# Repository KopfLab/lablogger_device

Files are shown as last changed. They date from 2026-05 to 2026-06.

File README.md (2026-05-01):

# *labLogger*

This repository holds the code, schematics, and documentation to build lab loggers. All content of this repository is free to use for noncommercial research and development efforts as outlined in the terms of the included [LICENSE file](LICENSE.md).

To cite ***labLogger*** in publications use:

> Kopf S, 2026. _labLogger: a Modular Internet Controllable LAB Equipment Logger_. <https://github.com/KopfLab/lablogger_device>

A BibTeX entry for LaTeX users is

```
@Manual{
  microLogger,
  title = {labLogger: a Modular Internet Controllable LAB Equipment Logger},
  author = {Sebastian Kopf},
  year = {2026},
  url = {https://github.com/KopfLab/lablogger_device}
}
```

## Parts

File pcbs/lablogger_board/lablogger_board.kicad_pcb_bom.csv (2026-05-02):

Designator | Quantity | Value | Footprint | Package | MPN | DNP | Mount_Type | Description | JLCPCB | JLCPCBURL | DigiKey | DigiKeyURL | STANDARD | MAXIMUM_PACKAGE_HEIGHT | MANUFACTURER | ParticleURL
C1, C2, C3, C4, C5, C6 | 6 | 100nF | C_0603 |  |  |  | smt | Unpolarized capacitor | C1591 | https://jlcpcb.com/partdetail/1943-CL10B104KB8NNNC/C1591
D1 | 1 | 1A/40V/500mV | D_DO-214AC_SMA |  | SS14 |  | smt | Diode 40 V 1A Surface Mount DO-214AC (SMA) | C83852 | https://jlcpcb.com/partdetail/onsemi-SS14/C83852 | SS14CT-ND | https://www.digikey.com/en/products/detail/onsemi/SS14/965474
D2, D3 | 2 | 3A/60V/750mV | D_DO-214AB_SMC |  | SS36 |  | tht | Diode 60 V 3A Surface Mount DO-214AB (SMC) | C391251 | https://jlcpcb.com/partdetail/onsemi-SS36/C391251 | SS36FSCT-ND | https://www.digikey.com/en/products/detail/onsemi/SS36/1053019
F1 | 1 | 24V/2.6A | Fuse_1812 |  | 2920L260/24DR |  | smt | Polymeric PTC Resettable Fuse 24V 2.6 A Ih Surface Mount 2920 (7351 Metric), Concave | C315904 | https://jlcpcb.com/partdetail/Littelfuse-2920L26024DR/C315904 | F6728CT-ND | https://www.digikey.com/en/products/detail/littelfuse-inc/2920L260-24DR/5427247
J10, J9 | 2 | 5mm | TERMINAL_BLOCK_1x03_5mm_vertical |  | TBP04R2-500-03BE |  | tht | 3 Position Terminal Block Header, Male Pins, Shrouded (4 Side) 0.197" (5.00mm) Vertical Through Hole |  |  | 2223-TBP04R2-500-03BE-ND | https://www.digikey.com/en/products/detail/same-sky-formerly-cui-devices/tbp04r2-500-03be/15775507 | Manufacturer Recommendations | 12.00mm
J11, J12 | 2 | DB9 | DB9_male |  | DE09P064TXLF |  | tht | 9 Position D-Sub Plug, Male Pins Connector |  |  | 609-1524-ND | https://www.digikey.com/en/products/detail/amphenol-cs-fci/DE09P064TXLF/1001838
J2 | 1 | Conn_01x07 | PIN_HEADERS_1X07 |  |  |  | tht | Basic 0.1" PTH
J3 | 1 | Conn_01x12 | PIN_HEADERS_1X12 |  |  |  | tht | Basic 0.1" PTH
J4 | 1 | PINHD-1X4 | PIN_HEADERS_1X04 |  |  |  | tht | Basic 0.1" PTH
J5, J6 | 2 | 5mm | TERMINAL_BLOCK_1x02_5mm_vertical |  | TBP04R2-500-02BE |  | tht | 2 Position Terminal Block Header, Male Pins, Shrouded (4 Side) 0.197" (5.00mm) Vertical Through Hole |  |  | 2223-TBP04R2-500-02BE-ND | https://www.digikey.com/en/products/detail/same-sky-formerly-cui-devices/TBP04R2-500-02BE/15775681 |  | 12.00mm | CUI Devices
J7, J8 | 2 | RJ11 | RJ11_MOLEX_955032641 |  | 0955032641 |  | tht | Jack Modular Connector 6p4c (RJ11, RJ14) Vertical Unshielded Cat3 |  |  | WM5579-ND | https://www.digikey.com/en/products/detail/molex/0955032641/1835871
P1 | 1 | 24V / 5A | PWR_JACK_PJ-064A |  | PJ-064A |  | tht | 2.0 mm Center Pin, 5.0 A, Vertical, Panel Mount, PC Pins, Dc Power Jack Connector |  |  | CP-064A-ND | https://www.digikey.com/en/products/detail/cui-devices/PJ-064A/2627221
Q1, Q2 | 2 | 5.7A / 30V | SOT-23-3 |  | AO3400A |  | tht | N-Channel 30 V 5.7A (Ta) 1.4W (Ta) Surface Mount SOT-23-3 | C20917 | https://jlcpcb.com/partdetail/Alpha_OmegaSemicon-AO3400A/C20917 | 785-1000-1-ND | https://www.digikey.com/en/products/detail/alpha-omega-semiconductor-inc/AO3400A/1855772
Q3, Q4 | 2 | 220mA / 50V | SOT-23-3 |  | BSS138 |  | tht | N-Channel 50 V 2200mA 350mW (Ta) Surface Mount SOT-23-3 | C52895 | https://jlcpcb.com/partdetail/onsemi-BSS138/C52895 | BSS138CT-ND | https://www.digikey.com/en/products/detail/onsemi/BSS138/244210
R1 | 1 | 150kΩ | R_1206 |  |  |  | smt | Resistor, US symbol | C17916 | https://jlcpcb.com/partdetail/18604-1206W4F1503T5E/C17916
R10 | 1 | 4.7kΩ | R_1206 |  |  |  | smt | Resistor, US symbol | C17936 | https://jlcpcb.com/partdetail/18624-1206W4F4701T5E/C17936
R11, R12, R13, R14, R2, R3, R4, R5, R7, R9 | 10 | 10kΩ | R_1206 |  |  |  | smt | Resistor, US symbol | C17902 | https://jlcpcb.com/partdetail/18590-1206W4F1002T5E/C17902
R15 | 1 | 120Ω | R_1206 |  |  |  | smt | Resistor, US symbol | C17909 | https://jlcpcb.com/partdetail/18597-1206W4F1200T5E/C17909
R6, R8 | 2 | 100Ω | R_1206 |  |  |  | smt | Resistor, US symbol | C17901 | https://jlcpcb.com/partdetail/18589-1206W4F1000T5E/C17901
U1 | 1 | 8-28V in / 5V 5W out | DC_DC_converter_R-78E5.0-1.0 |  | R-78E5.0-1.0 |  | tht | Linear Regulator Replacement DC DC Converter 1 Output 5V 1A 8V - 28V Input |  |  | 945-2201-ND | https://www.digikey.com/en/products/detail/recom-power/R-78E5-0-1-0/4930585
U2 | 1 | Particle2 / Boron | PHOTON2 |  | PHN2MEA / BRN404 |  | tht | Particle Photon 2 Wi-Fi enabled development kit |  |  |  |  |  |  |  | https://store.particle.io/collections/wifi/products/photon-2
U3 | 1 | RS485 Transceiver | 8-SOIC |  | SP3485 |  | smt | 1/1 Transceiver Half RS422, RS485 8-SOIC | C8963 | https://jlcpcb.com/partdetail/MaxLinear-SP3485EN_LTR/C8963 | 1016-1817-1-ND | https://www.digikey.com/en/products/detail/maxlinear-inc/SP3485EN-L-TR/2471929
U4 | 1 | RS232 Transceiver | TSSOP16_MXL |  | SP3232ECY-L |  | smt | 2/2 Transceiver Full RS232 16-TSSOP | C3028967 | https://jlcpcb.com/partdetail/MaxLinear-SP3232ECY_LTR/C3028967 | 1016-1105-5-ND | https://www.digikey.com/en/products/detail/maxlinear-inc/SP3232ECY-L/2411037

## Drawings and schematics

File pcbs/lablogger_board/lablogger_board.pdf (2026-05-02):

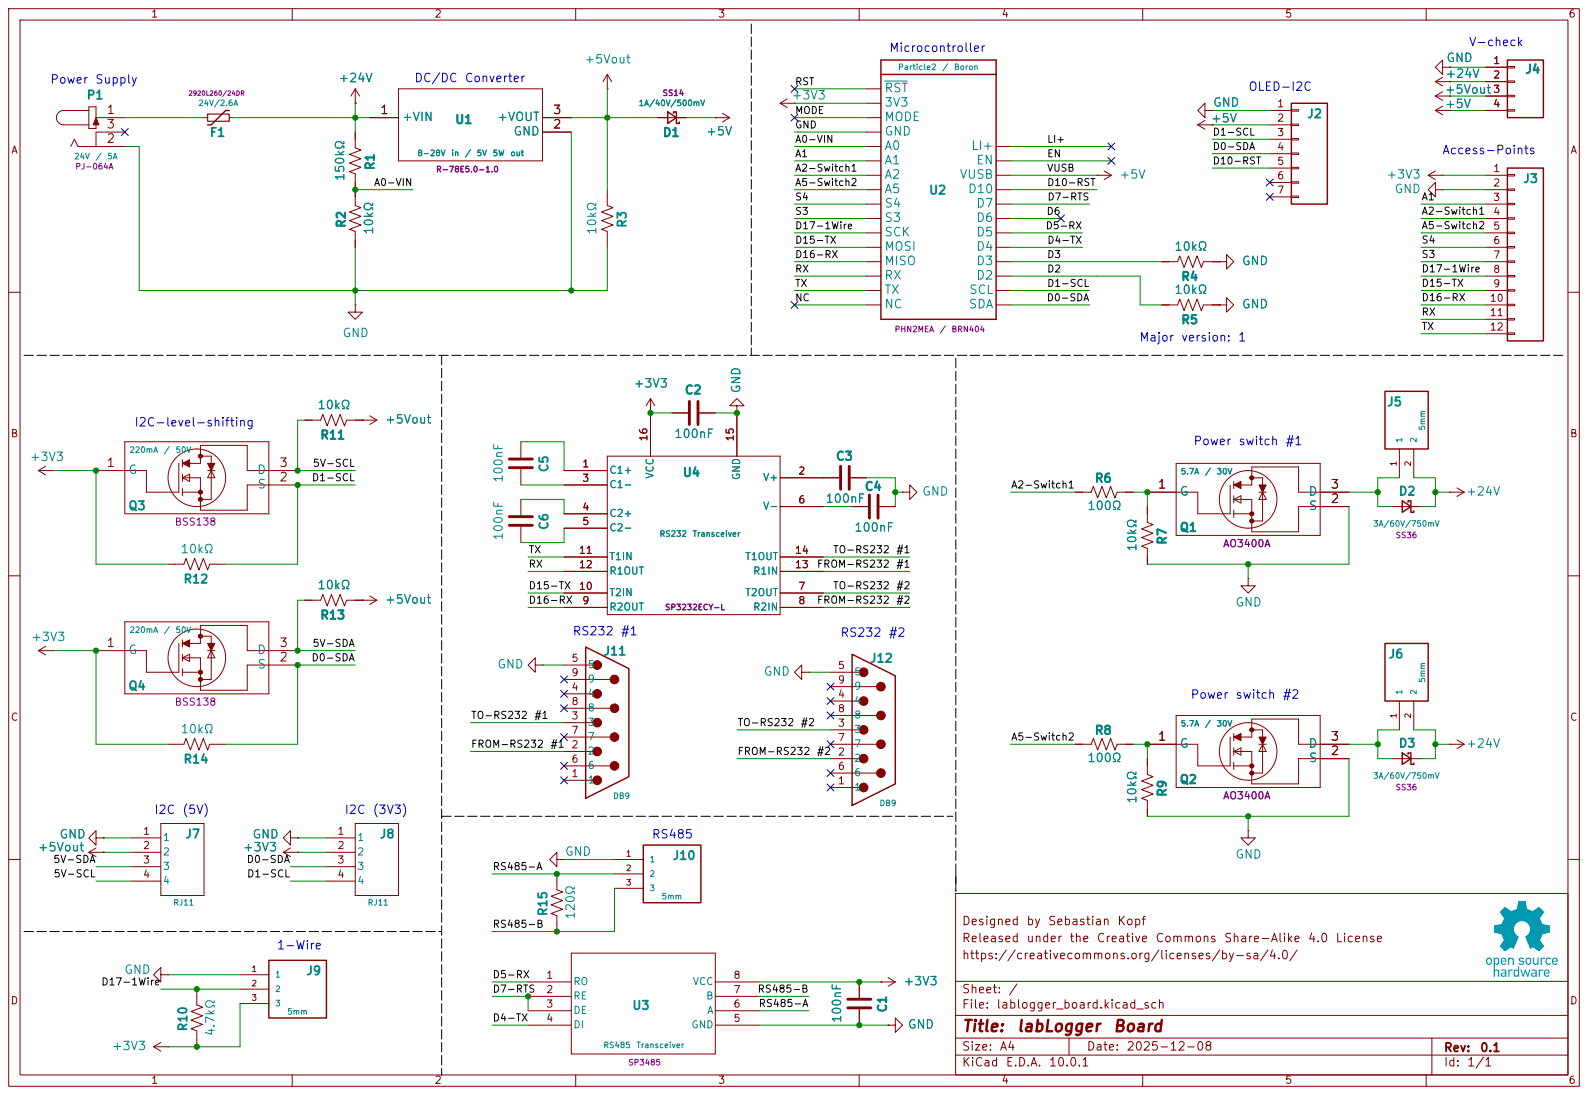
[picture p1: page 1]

5V-SCL D1-SCL D0-SDA D1-SCL

FROM-RS232 #1 D4-TX D7-RTS D5-RX RS485-A RS485-B

Designed by Sebastian Kopf
Released under the Creative Commons Share-Alike 4.0 License
https://creativecommons.org/licenses/by-sa/4.0/

Size: A4 | Rev: 0.1
KiCad E.D.A. 10.0.1 | Id: 1/1

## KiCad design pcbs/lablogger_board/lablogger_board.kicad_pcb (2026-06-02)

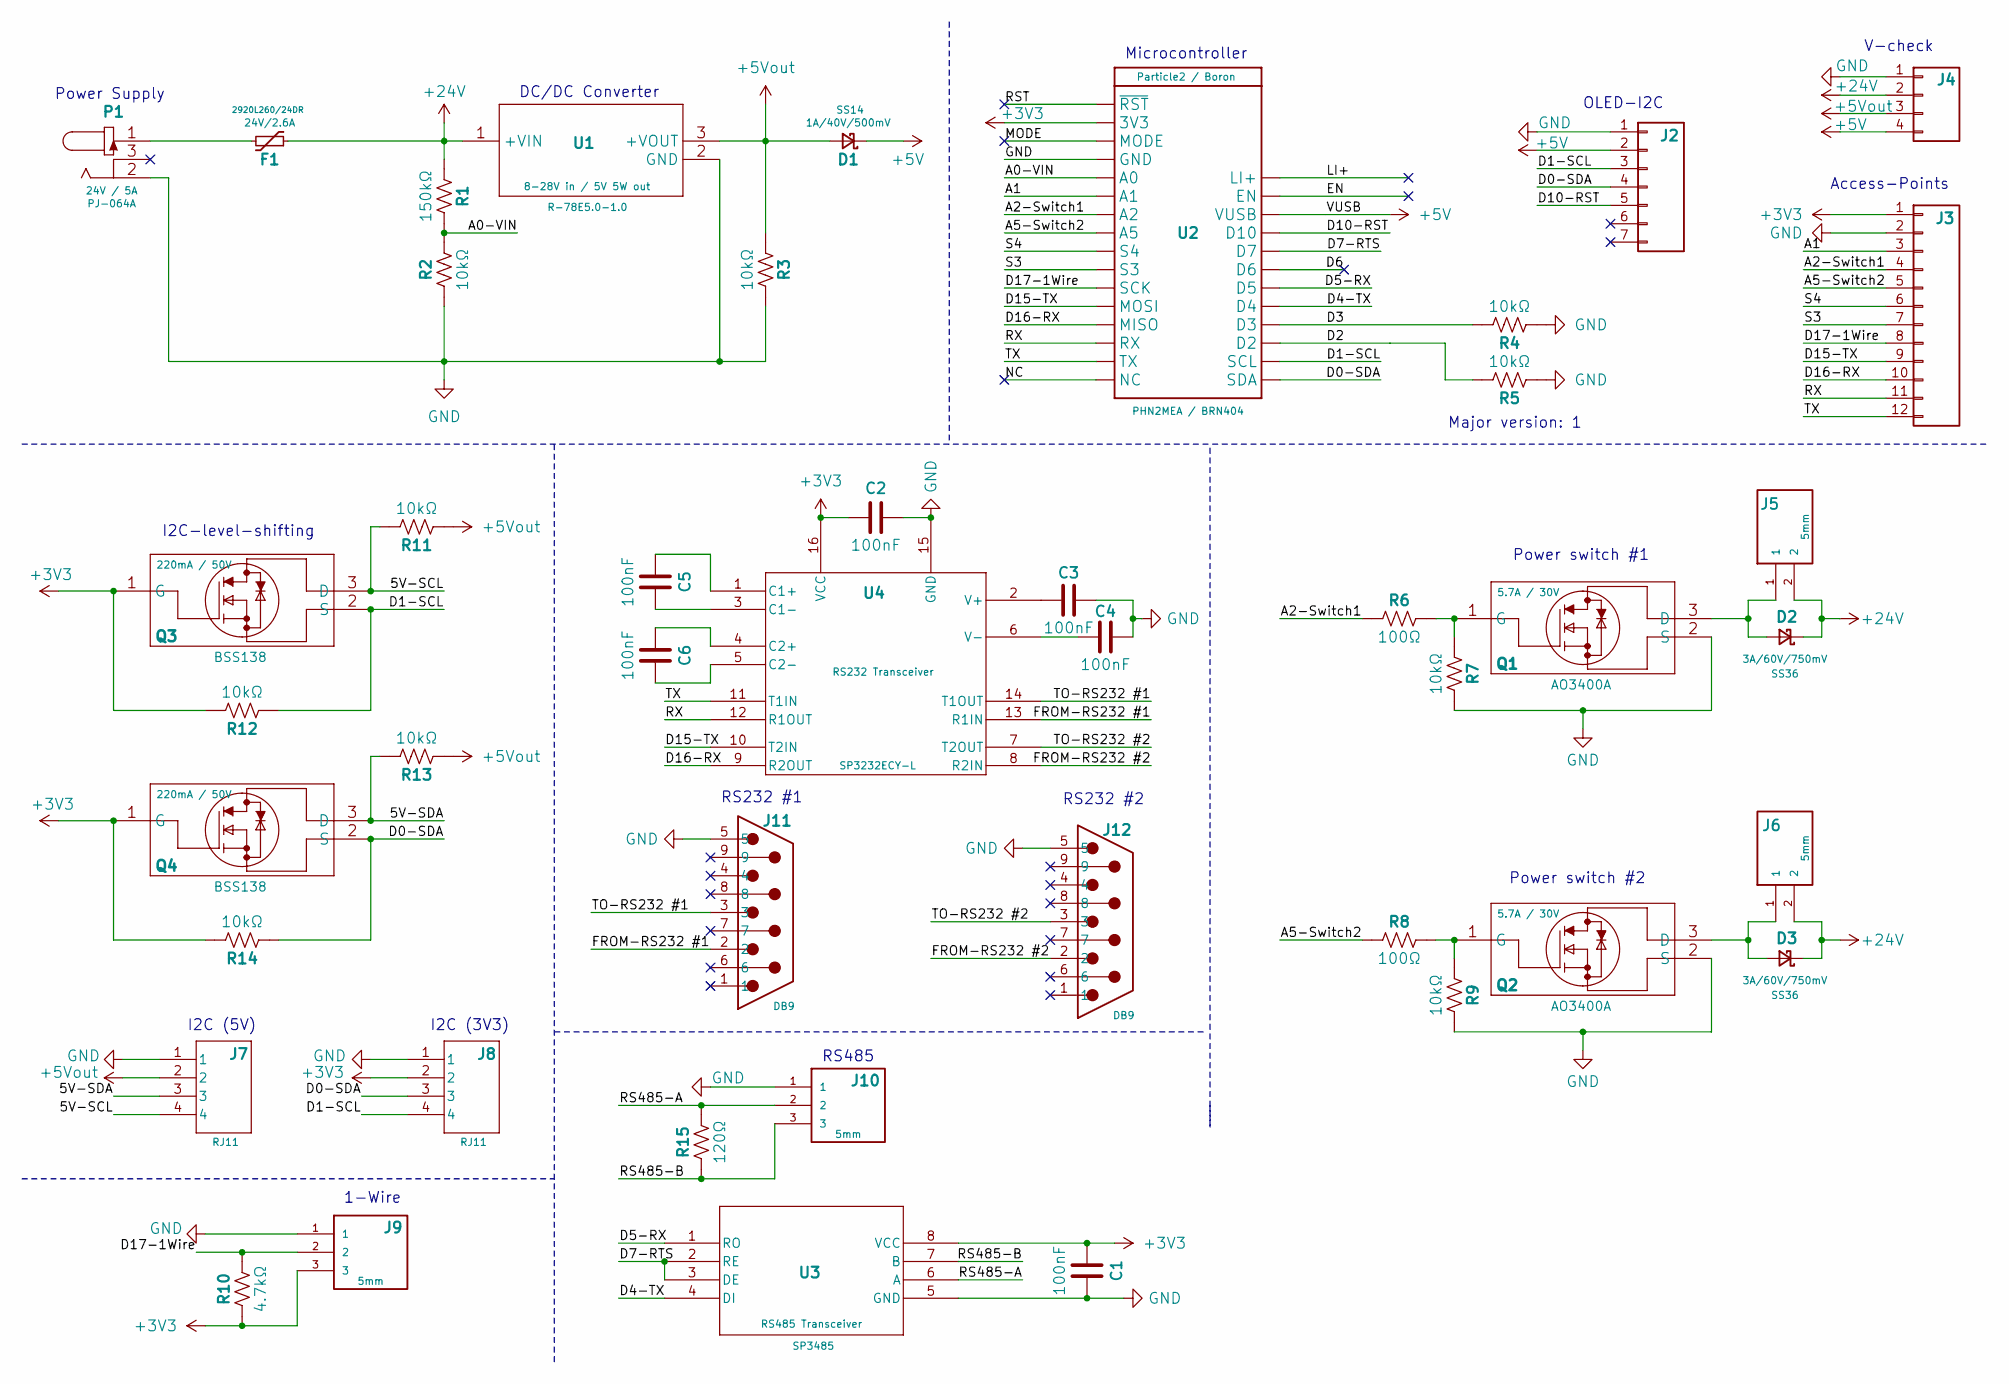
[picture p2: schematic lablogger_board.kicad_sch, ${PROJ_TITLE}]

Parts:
C1, C2, C3, C4, C6: 100nF; C_0603
C5: 100nF; C_0603; JLCPCB C1591
D1: 1A/40V/500mV; D_DO-214AC_SMA; MPN SS14; DigiKey SS14CT-ND
D2, D3: 3A/60V/750mV; D_DO-214AB_SMC; MPN SS36; DigiKey SS36FSCT-ND
F1: 24V/2.6A; Fuse_2920_7451; MPN 2920L260/24DR; DigiKey F6728CT-ND
J2: Conn_01x07; PIN_HEADERS_1X07
J3: Conn_01x12; PIN_HEADERS_1X12
J4: PINHD-1X4; PIN_HEADERS_1X04
J5, J6: 5mm; TERMINAL_BLOCK_1x02_5mm_vertical; MPN TBP04R2-500-02BE; DigiKey 2223-TBP04R2-500-02BE-ND
J7, J8: RJ11; RJ11_MOLEX_955032641; MPN 0955032641; DigiKey WM5579-ND
J9, J10: 5mm; TERMINAL_BLOCK_1x03_5mm_vertical; MPN TBP04R2-500-03BE; DigiKey 2223-TBP04R2-500-03BE-ND
J11, J12: DB9; DB9_male; MPN DE09P064TXLF; DigiKey 609-1524-ND
P1: 24V / 5A; PWR_JACK_PJ-064A; MPN PJ-064A; DigiKey CP-064A-ND
Q1, Q2: 5.7A / 30V; SOT-23-3; MPN AO3400A; DigiKey 785-1000-1-ND
Q3, Q4: 220mA / 50V; SOT-23-3; MPN BSS138; DigiKey BSS138CT-ND
R1: 150kΩ; R_1206; JLCPCB C17916
R2, R3, R4, R5, R7, R9, R12, R13, R14: 10kΩ; R_1206
R6, R8: 100Ω; R_1206; JLCPCB C17901
R10: 4.7kΩ; R_1206; JLCPCB C17936
R11: 10kΩ; R_1206; JLCPCB C17902
R15: 120Ω; R_1206; JLCPCB C17909
U1: 8-28V in / 5V 5W out; DC_DC_converter_R-78E5.0-1.0; MPN R-78E5.0-1.0; DigiKey 945-2201-ND
U2: Particle2 / Boron; PHOTON2; MPN PHN2MEA / BRN404
U3: RS485 Transceiver; 8-SOIC; MPN SP3485; DigiKey 1016-1817-1-ND
U4: RS232 Transceiver; TSSOP16_MXL; MPN SP3232ECY-L; DigiKey 1016-1105-5-ND

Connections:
+3V3: C1.1, C2.1, J3.1, J8.2, J9.3, Q3.1 (G), Q4.1 (G), R10.1, R12.2, R14.2, U2.2 (3V3), U3.8 (VCC), U4.16 (VCC)
+5V: D1.1 (K), J2.2, J4.4, U2.26 (VUSB)
+5Vout: D1.2 (A), J4.3, J7.2, R3.1, R11.1, R13.1, U1.3 (+VOUT)
+24V: D2.1 (K), D3.1 (K), F1.1, J4.2, J5.2, J6.2, R1.1, U1.1 (+VIN)
/5V-SCL: J7.4, Q3.3 (D), R11.2
/5V-SDA: J7.3, Q4.3 (D), R13.2
/A0-VIN: R1.2, R2.2, U2.5 (A0)
/A1: J3.3, U2.6 (A1)
/A2-Switch1: J3.4, R6.1, U2.7 (A2)
/A5-Switch2: J3.5, R8.1, U2.8 (A5)
/D0-SDA: J2.4, J8.3, Q4.2 (S), R14.1, U2.17 (SDA)
/D1-SCL: J2.3, J8.4, Q3.2 (S), R12.1, U2.18 (SCL)
/D2: R5.2, U2.19 (D2)
/D3: R4.2, U2.20 (D3)
/D4-TX: U2.21 (D4), U3.4 (DI)
/D5-RX: U2.22 (D5), U3.1 (RO)
/D6: U2.23 (D6)
/D7-RTS: U2.24 (D7), U3.2 (RE), U3.3 (DE)
/D10-RST: J2.5, U2.25 (D10)
/D15-TX: J3.9, U2.12 (MOSI), U4.10 (T2IN)
/D16-RX: J3.10, U2.13 (MISO), U4.9 (R2OUT)
/D17-1Wire: J3.8, J9.2, R10.2, U2.11 (SCK)
/EN: U2.27 (EN)
/FROM-RS232 #1: J11.2, U4.13 (R1IN)
/FROM-RS232 #2: J12.2, U4.8 (R2IN)
/LI+: U2.28 (LI+)
/MODE: U2.3 (MODE)
/NC: U2.16 (NC)
/RS485-A: J10.2, R15.2, U3.6 (A)
/RS485-B: J10.3, R15.1, U3.7 (B)
/RST: U2.1 (~RST)
/RX: J3.11, U2.14 (RX), U4.12 (R1OUT)
/S3: J3.7, U2.10 (S3)
/S4: J3.6, U2.9 (S4)
/TO-RS232 #1: J11.3, U4.14 (T1OUT)
/TO-RS232 #2: J12.3, U4.7 (T2OUT)
/TX: J3.12, U2.15 (TX), U4.11 (T1IN)
GND: C1.2, C2.2, C3.2, C4.2, J2.1, J3.2, J4.1, J7.1, J8.1, J9.1, J10.1, J11.5, J12.5, P1.2, Q1.2 (S), Q2.2 (S), R2.1, R3.2, R4.1, R5.1, R7.2, R9.2, U1.2 (GND), U2.4 (GND), U3.5 (GND), U4.15 (GND)
unnamed: D2.2 (A), J5.1, Q1.3 (D)
unnamed: D3.2 (A), J6.1, Q2.3 (D)
unnamed: F1.2, P1.1
unnamed: Q1.1 (G), R6.2, R7.1
unnamed: Q2.1 (G), R8.2, R9.1
unnamed: C5.1, U4.1 (C1+)
unnamed: C5.2, U4.3 (C1-)
unnamed: C6.1, U4.4 (C2+)
unnamed: C6.2, U4.5 (C2-)
unnamed: C3.1, U4.2 (V+)
unnamed: C4.1, U4.6 (V-)

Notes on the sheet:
Major version: 1
I2C (3V3)
Power switch #1
Microcontroller
Power Supply
1-Wire
I2C (5V)
DC/DC Converter
RS485
Access-Points
RS232 #2
RS232 #1
V-check
Power switch #2
I2C-level-shifting
OLED-I2C

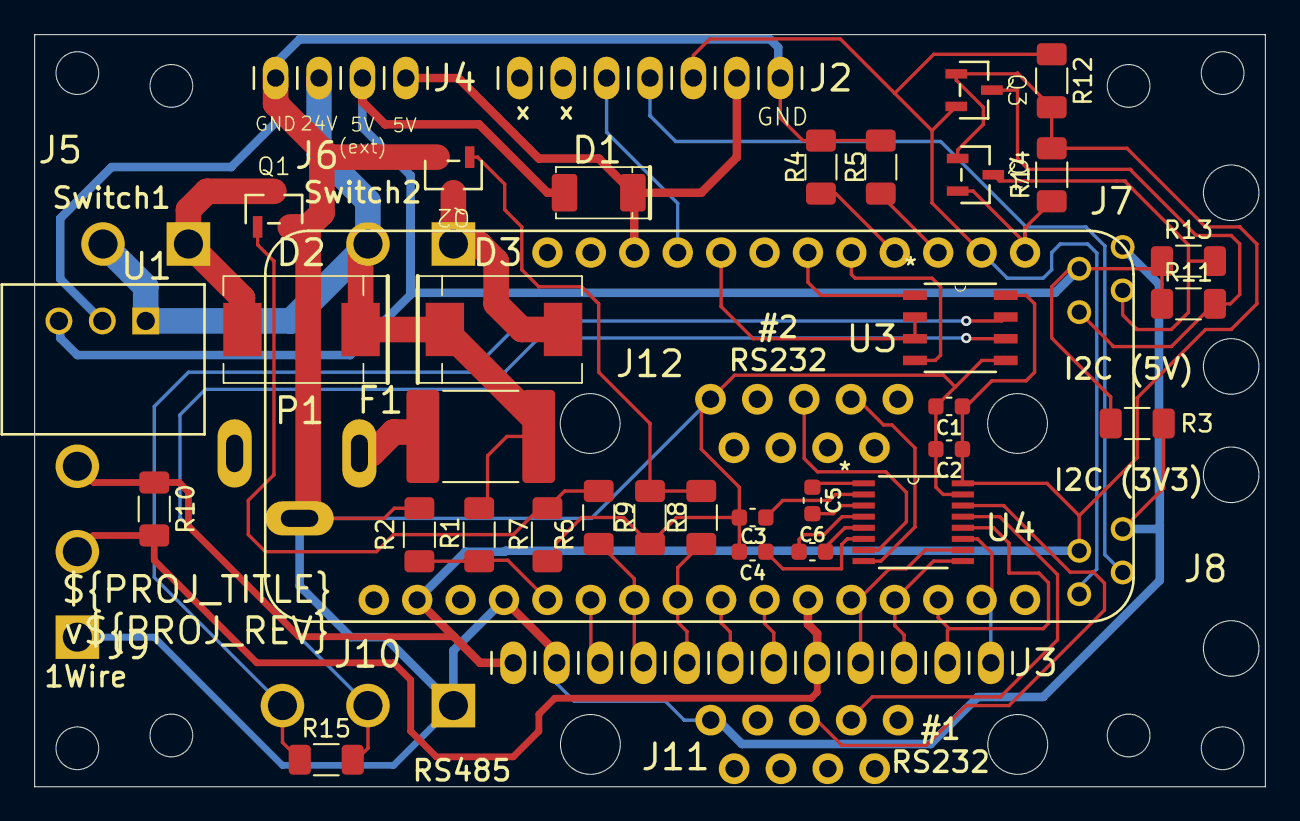
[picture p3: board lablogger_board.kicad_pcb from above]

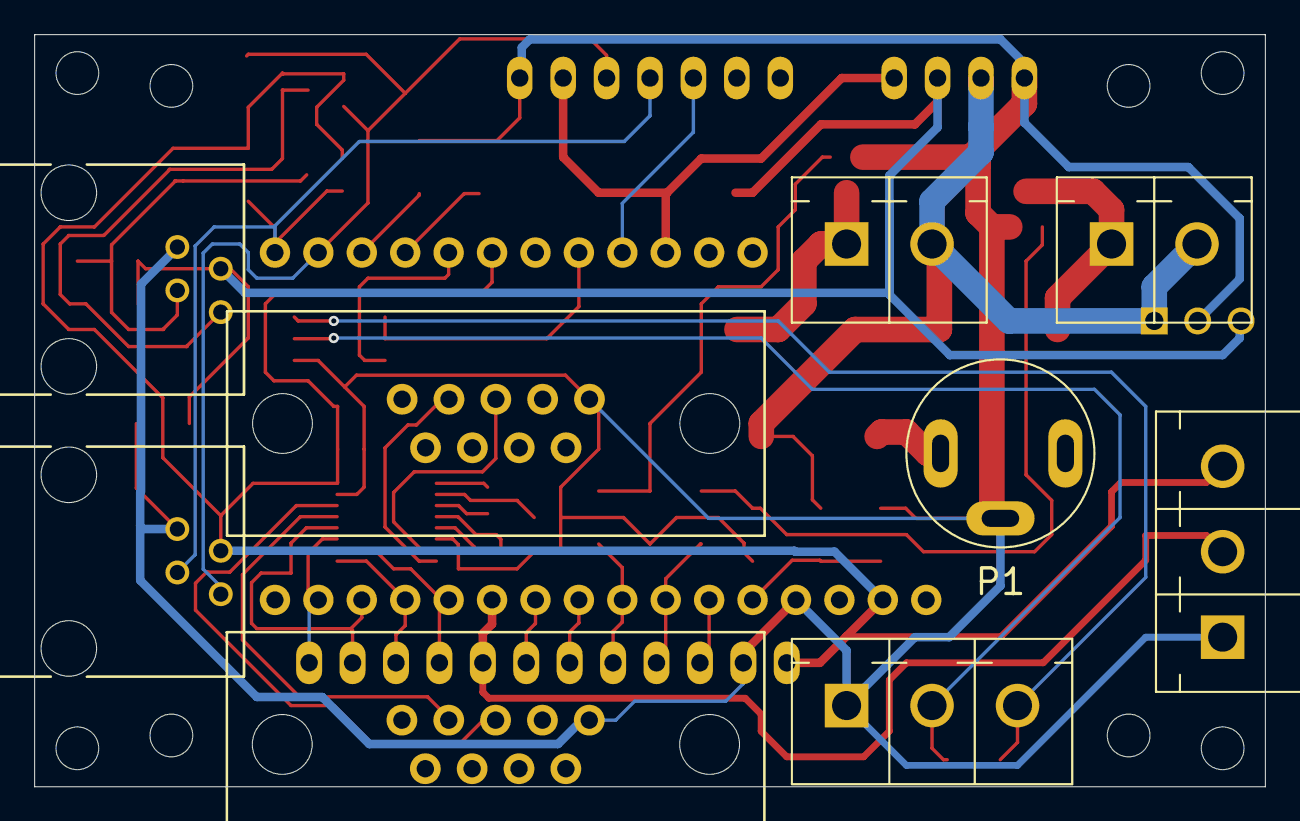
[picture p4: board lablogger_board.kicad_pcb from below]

Board: 2 copper layers, 72.0 x 44.0 mm, 53 parts (9 on the bottom side), 43 nets.

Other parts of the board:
H1, H2, H3, H4, H5, H6, H7, H8: MountingHole_2.5mm_M2.5

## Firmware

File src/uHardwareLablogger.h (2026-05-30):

#pragma once

#include "uTypedef.h"
#include "enums.h"
#include "uMultask.h"
#include "uParticleSystem.h"

// hardware parts
#include "uHardwareSensorVoltage.h"
#include "uHardwareDisplay.h"

// hardware constants
#define LABLOGGER_VOLTAGE_PIN A0
#define LABLOGGER_VOLTAGE_DIVIDER_REF 3.3
#define LABLOGGER_VOLTAGE_DIVIDER_R1 150.0
#define LABLOGGER_VOLTAGE_DIVIDER_R2 10.0
#define LABLOGGER_VOLTAGE_SCHOTTKY_DROP 0.0 // does not have a diode
#define LABLOGGER_CONTROLLER_VERSION_PIN1 D2
#define LABLOGGER_CONTROLLER_VERSION_PIN2 D3

/**
 * @brief hardware handler
 * uses a TmenuHandle for the convenience of sdds_vars but is not usually
 * included in the tree except for stand-alone testing
 */
class ThardwareLablogger : public TmenuHandle
{

private:
    // in case it is used in a tree
    Tmeta meta() override { return Tmeta{TYPE_ID, 0, "HARDWARE"}; }

public:
    // pcb versions
    class Tpcbs : public TmenuHandle
    {
    public:
        sdds_var(Tuint8, controller, sdds::opt::readonly);
    };
    sdds_var(Tpcbs, pcbVersions);
    // display
    sdds_var(ThardwareDisplay, display);
    // signals
    sdds_var(ThardwareSensorVoltage, voltage);

    // constructor
    ThardwareLablogger()
    {

        // run during setp
        on(sdds::setup())
        {

            // define pins
            pinMode(LABLOGGER_CONTROLLER_VERSION_PIN1, INPUT);
            pinMode(LABLOGGER_CONTROLLER_VERSION_PIN2, INPUT);

            // initialize hardware components (defines other pins)
            display.init(particleSystem().version.value());
            voltage.init(LABLOGGER_VOLTAGE_PIN, LABLOGGER_VOLTAGE_DIVIDER_REF, LABLOGGER_VOLTAGE_DIVIDER_R1, LABLOGGER_VOLTAGE_DIVIDER_R2, LABLOGGER_VOLTAGE_SCHOTTKY_DROP);

            // controller board version
            uint8_t b0 = digitalRead(LABLOGGER_CONTROLLER_VERSION_PIN1) ? 1 : 0;
            uint8_t b1 = digitalRead(LABLOGGER_CONTROLLER_VERSION_PIN2) ? 1 : 0;
            uint8_t version = (b1 << 1) | b0;
            pcbVersions.controller = version + 1;
        };

        // turn the voltage reader on
        voltage.state = enums::ToffOn::on;
    }
};

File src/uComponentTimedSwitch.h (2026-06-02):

#pragma once
#include "uTypedef.h"
#include "enums.h"
#include "uHardwarePwmOutput.h"

class TcomponentTimedSwitch : public TmenuHandle
{
public:
    // sdds enums
    sdds_enum(___, on, off, schedule) Taction;
    sdds_enum(on, off, schedule) Tstate;
    sdds_enum(on, off, error, undef) Tstatus;

    // sdds vars
    sdds_var(Taction, action);
    sdds_var(Tstate, state, sdds_joinOpt(sdds::opt::saveval, sdds::opt::readonly), Tstate::off);
    sdds_var(Tstatus, status, sdds::opt::readonly, Tstatus::undef);
    sdds_var(Tuint8, intensity_percent, sdds::opt::saveval, 100);
    sdds_var(Tuint32, scheduleOn_sec, sdds::opt::saveval, 60 * 60 * 12);  // 12 hours on
    sdds_var(Tuint32, scheduleOff_sec, sdds::opt::saveval, 60 * 60 * 12); // 12 hours off
    sdds_var(Tuint16, scheduleOnStart_HHMM, sdds::opt::saveval, 1200);
    sdds_var(Tstring, scheduleInfo, sdds::opt::readonly);

private:
    // hardware component
    ThardwarePwmOutput *FpwmOutput = nullptr;

    // schedule timer
    Ttimer FscheduleTimer;

    // schedule structure
    struct Schedule
    {
        bool isOn;
        uint32_t secondsToSwitch;
        uint8_t h, m, s;
    };

    Schedule calculateSchedule()
    {
        // schedule object
        Schedule r{false, 0, 0, 0, 0};

        // do we have a valid time?
        if (!Time.isValid())
            return r;

        // figure out how much time has past since the start (today or yesterday)
        const uint16_t start_hour = scheduleOnStart_HHMM.value() / 100;
        const uint16_t start_min = scheduleOnStart_HHMM.value() % 100;
        const uint32_t start_sec = start_hour * 60 * 60 + start_min * 60;
        const uint32_t now_sec = static_cast<uint32_t>(Time.hour()) * 3600 + Time.minute() * 60 + Time.second();
        const uint32_t delta = (start_sec > now_sec) ? 24 * 60 * 60 + now_sec - start_sec : now_sec - start_sec;

        // figure out which phase we are in and when the next phase starts
        const uint32_t period = scheduleOn_sec.value() + scheduleOff_sec.value();
        const uint32_t phase = delta % period;
        if (phase < scheduleOn_sec.value())
        {
            r.isOn = true;
            r.secondsToSwitch = scheduleOn_sec.value() - phase; // ON -> OFF
        }
        else
        {
            r.isOn = false;
            r.secondsToSwitch = period - phase; // OFF -> ON
        }

        // determine time to next in H:M:S
        uint32_t t = r.secondsToSwitch;
        r.h = (uint8_t)(t / 3600);
        t %= 3600;
        r.m = (uint8_t)(t / 60);
        r.s = (uint8_t)(t % 60);
        return r;
    }

    // update with current light state
    void update()
    {
        update(state);
    }

    // update hardware based on settings
    void update(Tstate::e _switchState)
    {
        // nothing happens if there's no hardware output
        if (!FpwmOutput)
            return;

        // switch on/off?
        bool on = false;
        if (_switchState == Tstate::off)
        {
            // off
            if (scheduleInfo != "")
                scheduleInfo = "";
        }
        else if (_switchState == Tstate::on)
        {
            // on
            on = true;
            if (scheduleInfo != "")
                scheduleInfo = "";
        }
        else if (_switchState == Tstate::schedule)
        {
            // schedule
            if (!Time.isValid())
            {
                // don't have valid time yet - keep off and reschedule check
                if (scheduleInfo != "pending")
                    scheduleInfo = "pending";
                FscheduleTimer.start(1000);
            }
            else
            {

                // determine schedule
                Schedule s = calculateSchedule();
                on = s.isOn;
                const dtypes::string next = (s.isOn) ? "off:" : "on:";

                // when to scheck back in?
                if (s.h == 0 && s.m == 0)
                {
                    scheduleInfo = next + dtypes::string(s.s) + "s";
                    FscheduleTimer.start(1000); // once a second
                }
                else if (s.h == 0)
                {
                    scheduleInfo = next + dtypes::string(s.m) + "m" + dtypes::string(s.s) + "s";
                    FscheduleTimer.start(1000); // once a second
                }
                else
                {
                    scheduleInfo = next + dtypes::string(s.h) + "h" + dtypes::string(s.m) + "m";
                    FscheduleTimer.start((s.s + 1) * 1000); // once we're down a minute
                }
            }
        }

        // update light
        int pwm = intensity_percent * 255 / 100;
        if (on)
        {
            FpwmOutput->pwm = pwm;
            FpwmOutput->state = enums::ToffOn::on;
        }
        else
        {
            FpwmOutput->state = enums::ToffOn::off;
        }
    }

public:
    // set hardware
    void setPwmOutput(ThardwarePwmOutput *_output)
    {
        if (_output)
        {
            FpwmOutput = _output;
            // update switch status from hardware
            on(FpwmOutput->state)
            {
                if (FpwmOutput->state == enums::ToffOn::on && status != Tstatus::on)
                    status = Tstatus::on;
                else if (FpwmOutput->state == enums::ToffOn::off && status != Tstatus::off)
                    status = Tstatus::off;
            };
            FpwmOutput->state.signalEvents();
        }
    }

    // constructor
    TcomponentTimedSwitch()
    {
        // timer
        on(FscheduleTimer)
        {
            update();
        };

        // switch action events
        on(action)
        {
            // stop if no action
            if (action == Taction::___)
                return;

            // process actions
            if (action == Taction::on)
            {
                state = Tstate::on;
                update();
            }
            else if (action == Taction::off)
            {
                state = Tstate::off;
                update();
            }
            else if (action == Taction::schedule)
            {
                state = Tstate::schedule;
                update();
            }

            // reset action
            action = Taction::___;
        };

        // change switch intensity
        on(intensity_percent)
        {
            if (intensity_percent == 0)
                intensity_percent = 1;
            else if (intensity_percent > 100)
                intensity_percent = 100;
            else
                update();
        };

        // schedule
        on(scheduleOn_sec)
        {
            if (scheduleOn_sec == 0)
                scheduleOn_sec = 1;
            else
                update();
        };
        on(scheduleOff_sec)
        {
            if (scheduleOff_sec == 0)
                scheduleOff_sec = 1;
            else
                update();
        };
        on(scheduleOnStart_HHMM)
        {
            if (scheduleOnStart_HHMM > 2359)
                scheduleOnStart_HHMM = 0;
            else
                update();
        };
    }
};

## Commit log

2026-05-01 lablogger pcb first draft
    [lablogger_board.kicad_pcb, lablogger_board.kicad_sch]
2026-05-02 lablogger first version
    [lablogger_board.kicad_pcb, lablogger_board.kicad_pcb_bom.csv, lablogger_board.kicad_sch]
2026-05-29 basic repo setup for device firmware
2026-06-02 update pcb to version 0.3: make holes for db9 connectors bigger
    [lablogger_board.kicad_pcb]
